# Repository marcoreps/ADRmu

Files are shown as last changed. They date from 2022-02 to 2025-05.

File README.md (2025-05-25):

# ADR1000 10V standard

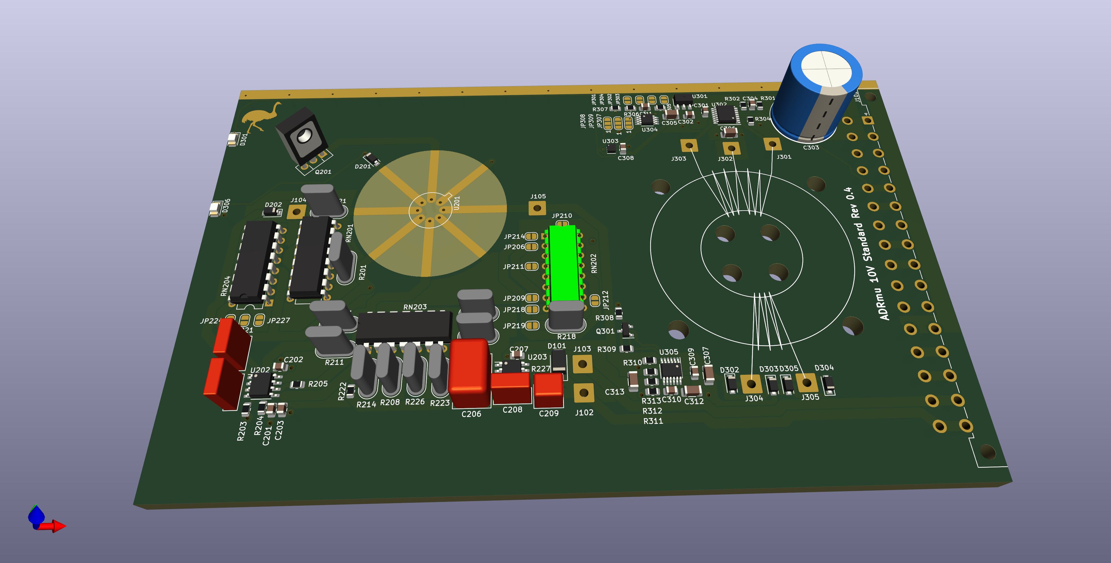
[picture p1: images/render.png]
rendering

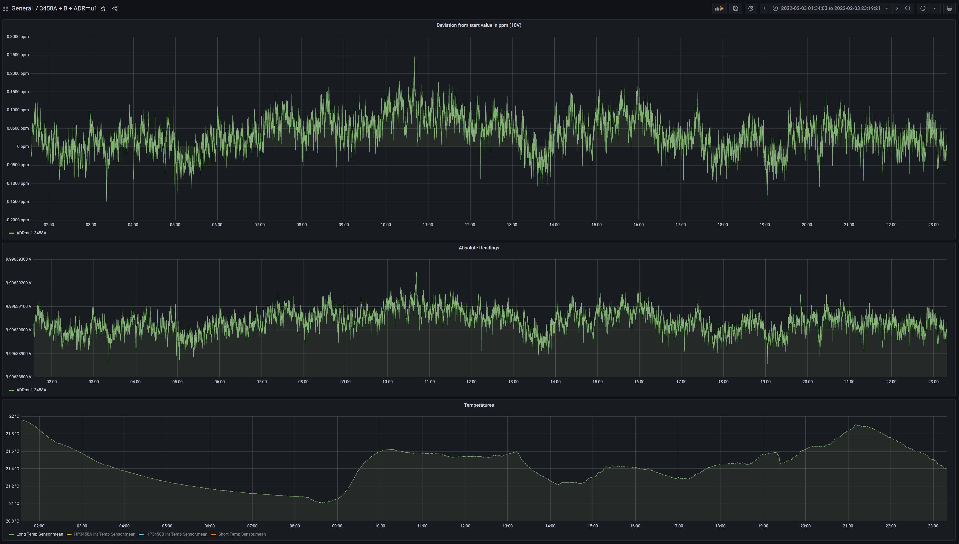
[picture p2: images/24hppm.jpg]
ppm over 24h

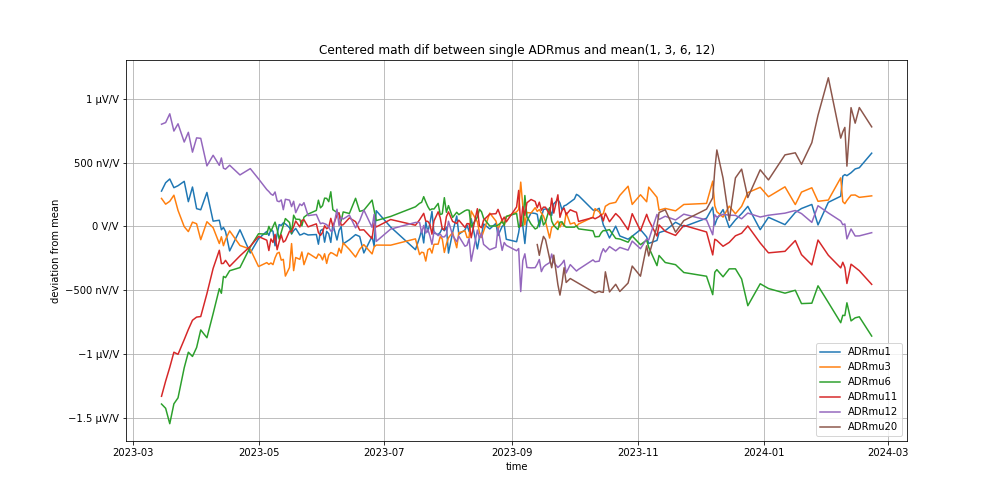
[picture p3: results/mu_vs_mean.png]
one year drift


## Scope

Low cost 10V DC reference standard in DIN 41612 modular enclosure. Based on ovenized LTZ1000 / LTZ1000A or ADR1000A zener diodes. Fits into standard 100x160mm project boxes too. The most promising strategies for configuring the zener and buffering the output are accommodated. Includes a high isolation DC-DC converter to attenuate the effects of common mode current.

## TODO

Align JP and R designators

Remove JPB and JPH enumeration

add lt5400 and other gain resistor options

discrete push-pull driver

snubber for the DC-DC converter?

## Assembly advice

Recommended 5:7 transformer (pri:sec) when using 12V input

## Spec speculations

After initial settling, tempco adjustment, continuously powered on, no ambient temperatures outside of specified range

### Output Voltage Stability (± µV/V):

24 hour: < 0.3

30 day: < 0.4

90 day: < 0.8

1 year: < 1.0

### Output Voltage Noise (0.1 - 10 Hz)(±µV/V rms)

< 0.02

### Output Voltage Tempco (±µV/V/K)

< 0.04

### Short circuit current (mA)

9-11

### Power consumption (W)

\< 2W

### Isolation (to DCin, Chassis)

\> 10 000 MΩ

< 1000 pF

### Output Protection

Output can be shorted indefinitely with battery life derating. Output protected against ESD and input up to 60V.

### Specified Temperature Range (°C)

15 - 35

### Oerational Temperature Range (°C)

-10 - 40

## Measured results
| SN    | U202  | .1-10Hz Noise   | Tempco 15-35°C    |  24h Stab  |  30d Stab  |  90d Stab  |  1yr Stab  |
| ---   | ----  | --------------  | ---------------   | ---------- | ---------- | ---------- | ---------- |
|       |       | \[µV/V rms\]    | \[µV/V/k\]        | \[µV/V\]   | \[µV/V\]   | \[µV/V\]   | \[µV/V\]   |
|   1   | ADR   | [0.0139][1]     |                   | 0.25       | 0.4        |            |            |
| ~~2~~ |~~LTZ-A~~| ~~[0.0175][2]~~|                  |            |            |            |            |
|   3   | LTZ-A | [0.0201][3]     | [-0.024][3tc]     |            |            |            |            |
|   4   |ADR1001| [0.0275][4]     | [-0.133][4tc]     |            |            |            |            |
| ~~5~~ |~~ADR~~|~~[0.0119][5]~~  |~~[+0.015][5tc]~~  |            |            |            |            |
| ~~7~~ |~~ADR~~|~~[0.0125][7]~~  |~~[+0.032][7tc]~~  |            |            |            |            |
|   9   |  ADR  |  [0.0121][9]    |  [+0.156][9tc]    |            |            |            |            |
|~~107~~|~~ADR~~|                 |~~[+0.049][107tc]~~|            |            |            |            |
|~~108~~|~~ADR~~|~~[0.0163][108]~~|~~[+0.030][108tc]~~|            |            |            |            |
|~~10~~ |~~ADR~~|~~[0.0115][10]~~ |~~[-0.028][10tc]~~ |            |            |            |            |
|  11   | ADR   | [0.0129][11]    | [+0.015][11tc]    |            |            |            |            |
|  12   | ADR   | [0.0116][12]    |                   |            |            |            |            |
|~~13~~ |~~ADR~~|~~[0.0132][13]~~ |~~[-0.024][13tc]~~ |            |            |            |            |
|~~F731B~~  |~~DH80417B~~| ~~[0.0272][731]~~  |       |            |            |            |            |
|   6   | ADR   |                 | [-0.018][6tc]     |            |            |            |            |
|~~14~~ |~~LTZ-A~~|               |~~[+0.025][14tc]~~ |            |            |            |            |
|  15   |  ADR  |   [0.0123][15]  |                   |            |            |            |            |
|  20   | LTZ-A |                 | -0.018            |            |            |            |            |
 
[1]:/results/ADRmu1_LFnoise.png
[2]:/results/ADRmu2_LFnoise.png
[3]:/results/ADRmu3_LFnoise.png
[4]:/results/ADRmu4_LFnoise_improved.png
[5]:/results/ADRmu5_LFnoise.png
[7]:/results/ADRmu7_LFnoise.png
[9]:/results/ADRmu9_LFnoise.png
[10]:/results/ADRmu10_LFnoise.png
[11]:/results/ADRmu11_LFnoise.png
[12]:/results/ADRmu12_LFnoise.png
[13]:/results/ADRmu13_LFnoise.png
[13]:/results/ADRmu15_LFnoise.png
[108]:/results/ADRmu108_LFnoise.png
[731]:/results/Fluke731B_LFnoise.png

[3tc]:/results/ADRmu3_TC.ipynb
[4tc]:/results/ADRmu4_TC.ipynb
[5tc]:/results/ADRmu5_TC.ipynb
[7tc]:/results/ADRmu7_TC.ipynb
[9tc]:/results/ADRmu9_TC.ipynb
[10tc]:/results/ADRmu10_TC.ipynb
[11tc]:/results/ADRmu11_TC.ipynb
[12tc]:/results/ADRmu12_TC.ipynb
[13tc]:/results/ADRmu13_TC.ipynb
[107tc]:/results/ADRmu107_TC.ipynb
[108tc]:/results/ADRmu108_TC.ipynb
[14tc]:/results/ADRmu14_TC.ipynb
[6tc]:/results/ADRmu6_TC.ipynb

Strikethrough: Device no longer in my possession

## Initial drift & burn-in
| SN  | PCB  |      U202      | Powered on | Preparation | Initial ΔV | Hours to plateau | .1-10Hz noise before | Special |
| --- | ---- | -------------- | ---------- | ----------- | ---------- | ---------------- | -------------------- |---------|
|   1 | 0.4  | ADR1000A 2017  | Jul 2021   |1yr dummy circuit| no data|                  |                      | VPG golden network |
|   2 | 0.4  |    LTZ1000A    | Apr 2022   | none        | no data    |                  |                      | LTZ1000A w/ VPG foil |
|   3 | 0.5  |    LTZ1000A    | Mar 2022   | none        | no data    |                  |                      | Cheapest LTZ variant |
|   4 |0.5SE |    ADR10001    | May 2022   | none        | no data    |                  |                      | ~~Popcorn noise~~ Healed? |
|   5 | 0.9  | ADR1000A 2022  | Jan 2023   | 7d 150°C b&b|            |                  |                      | Gone to new owner |
|   7 | 0.9  | ADR1000A 2022  | Jan 2023   | 7d 150°C b&b|            |                  |                      | No trim resistors |
|   9 | 0.9  | ADR1000A 2022  | Jan 2023   | none        | 1.1 µV/V   | 310              |                      | VPG golden network |
| 107 | 0.9  | ADR1000A 2018  | Dec 2022   | none        | 3.8 µV/V   | 640              |                      | Transplant to 108 |
| 108 | 0.9  | ADR1000A 2018  | Dec 2022   | none        | 3.8 µV/V   | 640              |                      | Gone to new owner |
|  10 | 0.9  | ADR1000A 2022  | Feb 2023   | none        |            |                  |                      | On/off cylcing 48h |
|  11 | 0.9  | ADR1000A 2022  | Feb 2023   |7d dummy circuit|         |                  |                      | No trim resistors |
|  12 | 0.9  | ADR1000A 2022  | Feb 2023   |7d in situ b&b|           |                  |                      | On/off cylcing 24h |
|  13 | 0.9  | ADR1000A 2022  | Feb 2023   |             |            |                  |                      | Ultrasonic cleaned |
|   6 | 1.1  | ADR1000A 2022  | Mar 2023   |30d dummy circuit|        |                  |                      | Chinese SMT assembly |
|  14 | 1.1  | LTZ1000A 2020  | Mar 2023   | none        |            |                  |                      | Chinese SMT assembly |
|  15 | 1.1  | LTZ1000A 2020  | Mar 2023   | none        |            |                  |                      | Chinese SMT assembly |
|  44 | 1.1  | LTZ1000A 2020  | Mar 2023   | none        |            |                  |                      | Chinese SMT assembly |
|  20 | 1.1  | LTZ1000A 2020  | Sep 2023   | none        |            |                  |                      | Chinese SMT assembly |

## Trim levels

The PCB is prepared for various configurations to adapt to different needs and part availabilities. Here's what I have built so far:

| SN  | U202 | R213 / Pin4 | R214 / Pin5 | R220 / Pin3 | Oven divider      | R225 / Iz Down | R223 / Iz Up | 10V gain divider |
| --- | ---- | ----------- | ----------- | ----------- | ----------------- | -------------- | ------------ | ---------------- |
|   1 | ADR  | 1445 95.3R  | 1445 61.9k  | 0R          | 1445 13 ratio     | open           | open         | 1445 2 ratio     |
|   2 |LTZ-A | Z201 100R   | 61.9k  Foil | SMD Foil    | VHD200 13 ratio   |                |              | VHD200 2.5 ratio |
|   3 |LTZ-A | 100R TOMC   | 50k S102    | 100R TOMC/5 | TDP10k 13.5 ratio | open           | 230k RN73    | TDP10k 2.5 ratio |
|   4 |ADR1k1| 100R VHP100T| integrated  | integrated  | integrated        |                |              | integrated       |
|   5 | ADR  | Alpha MCY   | Alpha MAY   | 0R          | TDP10k 11.5 ratio | open           | 470k RN73    | TDP10k 2 ratio   |
|   7 | ADR  | Z201        | Z201        | 0R          | TDP10k            | open           | open         | TDP10k 2 ratio   |
|   9 | ADR  | 1445 95.3R  | 1445 61.9k  | 0R          | 1445 13 ratio     | open           | open         | 1445 2 ratio     |
| 107 | ADR  | Z201T       | Z202T       | 0R          | TOMC10k 11.5 ratio| 200k RN73      | open         | TDP10k 2 ratio   |
| 108 | ADR  | Z201T       | Z202T       | 0R          | TOMC10k 11.5 ratio|                |              | TDP10k 2 ratio   |
|  10 | ADR  | RCK02       | RCK02       | 0R          | TDP10k 11.5 ratio | 493k RN73      | open         | TDP10k 2 ratio   |
|  11 | ADR  | Z201T       | Z201T       | 0R          | TDP10k 11.5 ratio |                |              | TDP10k 2 ratio   |
|  12 | ADR  | RCK02       | RCK02       | 0R          | TDP10k 12 ratio   | 1M             | open         | TDP10k 2 ratio   |
|  13 | ADR  | RCK02       | RCK02       | 0R          | TDP10k 11.5 ratio | open           | 1M           | TDP10k 2 ratio   |
|   6 | ADR  | PTF56       | PTF56       | 0R          | TDP10k 11.5 ratio |                |              | TDP10k 2 ratio   |
|  14 |LTZ-A | TDP         | 1% ax metal | TDP         | TDP10k 12   ratio | open           | open         | TDP10k 2.5 ratio |
|  15 |      |             |             |             |                   |                |              |                  |
|  44 | ADR  | Z201T       | Z202T       | 0R          | TDP10k 11.5 ratio | 900k           | open         | TDP10k 2 ratio   |
|  20 |LTZ-A | 100R TDP    | 40k Prec WW | 16.667R TDP | TDP10k 11.5 ratio | open           | 1M           | TDP10k 2.5 ratio |

## Raw Vz of 10 parts in datasheet default circuit, warmed up for a few minutes but not burnt in
| SN  |   Type  | Datecode |     Vz    | 
| --- | ------- | -------- | --------- |
| \#1 | ADR1000 | 2108     | 6.6556730 |
| \#8 | ADR1000 | 2108     | 6.6545676 |
| \#9 | ADR1000 | 2108     | 6.6531460 |
| \#10| ADR1000 | 2108     | 6.6609841 |
| \#11| ADR1000 | 2108     | 6.6690263 |
| \#12| ADR1000 | 2108     | 6.6534043 |
|   5 | ADR1000 | 2209     | 6.6457519 |
|   8 | ADR1000 | 2209     | 6.6509818 |
|   3 | ADR1000 | 1839     | 6.6707478 |
| \#7 | ADR1000 | 2108     | 6.6545726 |

### ADR1000 & Vishay 1445 All-in-one Resistor Network

My SN 1 is built this way. This is a no-brainer or easy mode. When I got my first glimpse at the ADR1000 datasheet I went straight to Vishay Foil Resistors and ordered an all-in-one resistor network with all the critical resistors from the datasheet plus a simple divider for buffering the 6.62V output to 10V ([Custom network specification][1445]). By specifying at least 2 ppm/°C TC tracking for the two critical dividers I am guaranteed great performance. And thanks to the hermetically sealed DIP14 package I expect little long term drift from the resistors. This solution comes at a hefty price and is not effortlessly adjustable after assembly.

[1445]:/datasheets/322146_p1-4_1445_Marco_Reps.pdf

### LTZ1000A & Discrete Vishay Foil Resistors

My SN 2 is built this way. This is probably the most popular way of building LTZ1000 voltage standards (i.e. [xDevs KX][kx]). Digikey carries quite a few hermetically sealed Vishay Bulk Metal Foil resistors ~~without MOQ these days~~ not any more LAME!, giving you all the design freedom. The two most critical parts are the LTZ-temperature-configuration divider i.e. 13k/1k and the 7.1V to 10V buffer divider i.e. 2k/5k. For these two I used hermetically sealed Vishay VHD200 dividers. These have guaranteed TC tracking and little long term drift. The remaining LTZ-configuration resistors i.e. 70k, 70k, 120R are not very critical. For best performance you can add an additional resistor to LTZ pin 3 to improve the Vrefs tempco, see "Adjusting Temperature Coefficient in Unstabilized Applications" in the LTZ1000 datasheet. 20 Ohm seems to be a reasonable approximation, suitable for most LTZs. In my case I determined 18 Ohm to be an optimal resistor with a TC peak at the oven setpoint. Careful, this additional resistor, if equipped, has a lot of influence on zener voltage and should be of high quality.

[kx]:https://xdevs.com/article/kx-ref/

### LTZ1000A & Thin film arrays

My SN 3 and 20 are built this way. This variant is inspired by Datron Wavetek 7000 DCV Standards ([EEVBlog forum thread][w7000]) and as such it has proven itself over a long time. Here the most critical voltage dividers for the LTZ1000 temperature and the 7->10V gain are implemented through an arrangement of monolithic thin film resistor arrays and their fantastic tracking temperature coefficients. Furthermore the overall output voltage tempco is fine-tuned after assembly through trim resistors R225 / R223. SN 3 is one of the cheapest ADRmus in my comparison, yet one of the most stable ones.

[w7000]:https://www.eevblog.com/forum/metrology/(3300)-wavetek-7000-the-hidden-gemstone/

### ADR1000 & Thin film arrays

Most of my ADRmus are built this way. This is the most cost-effective way to build a great performance 10V DC Standard. The same techniques that worked for LTZ in the past also apply to ADR1000, only the specific resistor values are slightly different. Based on my early ADR1000 samples I can see significantly longer initial settling times of ADR1000, which can be improved simply by power cycling a part in its default circuit (30 minutes off, 30 minutes on for a week). This new part exhibits lower low frequency noise than LTZ. A 10V buffer circuit with a low noise op amp and thin film arrays ([Excess Noise in Thin Film and Metal Foil Resistor Networks][beev]) passes this advantage right on to the output. 

[beev]:https://arxiv.org/abs/2109.02448

### ADR1001

I have been given one very early sample of this new part, so my results may not reflect the final parts performance. This new all-in-one ovenized zener reference & buffer makes it easier than ever before to deploy a high performance, environmentally tolerant voltage reference with few external parts and little research. My sample showed some popcorn noise at first ([Screenshot][popcorn]), which I seemingly improved by keeping the part powered on, externally heated to 110°C for a few weeks. This extreme measure made it impossible to judge early drift. Long-term drift and tempco now seem to fall easily within the datasheet spec. LF noise of the 10V output still appears to be slightly elevated, but the datasheet only specifies this for the 6P6 output. Overall this part is not the greatest performer in my comparison, it lacks a way of fine-tuning, but it's by far the easiest to use and its efficient overall heater makes it interesting for portable devices.

[popcorn]:/results/ADRmu4_LFnoise_popcorn.png

## Results

### Raw data

Unprocessed CSV files can be found here https://github.com/marcoreps/multiinstrumentalist/tree/master/csv These show direct readings by digital voltmeters, which are subject to temperature variations, adjustments and even modifications, resulting in large deviations of readings.

### Processed data

To attenuate voltmeter errors from the measurements, we use the mathematical difference between an ADRmu reading and the average of many ADRmu readings that were taken at the same time, with the same voltmeter. These results can be found here https://github.com/marcoreps/ADRmu/tree/main/results

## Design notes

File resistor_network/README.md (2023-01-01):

## Scope

This is an adapter for up to 8 SMD resistors to fit into a DIP16 footprint. Using this board one could assemble an all-in-one LTZ/ADR configuration and buffering resistor network out of good quality SMD thin film resistors such as RN73. When using a thermally conductive PCB substrate such as Al, Cu, AlN or Al2O3 the resistors are thermally coupled which can be an advantage. When populating the crystal heater circuit and providing it with power, Vref and GND, it will thermally stabilize the resistor networks temperature at around 40°C.

## Result

I have performed only one superficial test with such a network so far and it didn't look as good as the monolithic 8xthin film array method.

## Image

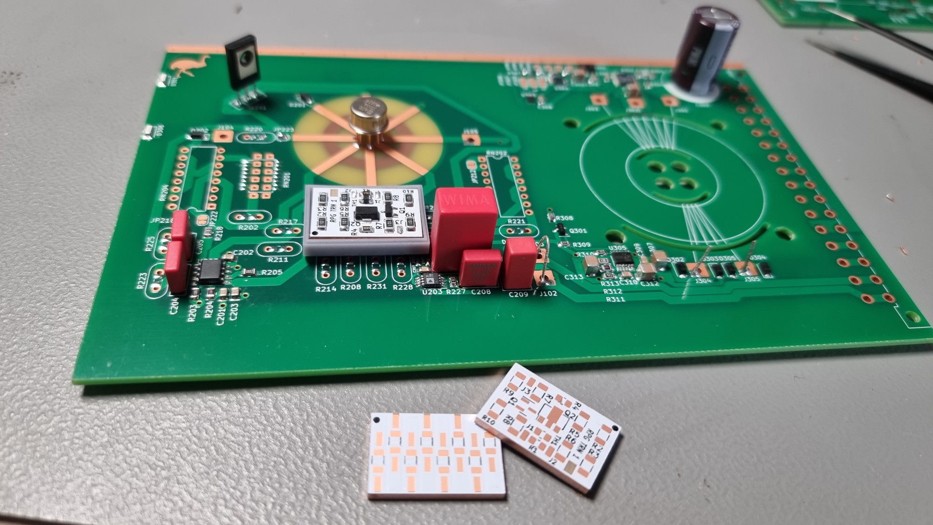
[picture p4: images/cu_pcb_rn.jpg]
serviervorschlag


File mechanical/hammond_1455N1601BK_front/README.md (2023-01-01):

# Careful:

The + / - Cutouts are for special Taobao connectors, too small for Pomona 3770! Adjust to your needs before ordering!

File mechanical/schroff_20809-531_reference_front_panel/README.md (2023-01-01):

# Front panel for Schroff 20809-531 Eurocard cassettes 

Very ugly silk screen, would not recommend this design, but the hole locations fit.

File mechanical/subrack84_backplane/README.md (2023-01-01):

# 4 + 4 Module Backplane

Tested successfully with PROMA 133061 aka https://www.reichelt.com/de/en/system-housing-geh-sg-1-10-p50437.html but should be compatible with many other eurocard subrack enclosures.

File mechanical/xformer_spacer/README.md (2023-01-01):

# DC-DC Transformer spacer for the reference module

Optional part to help reduce inter-winding capacitance, inspired by Mac

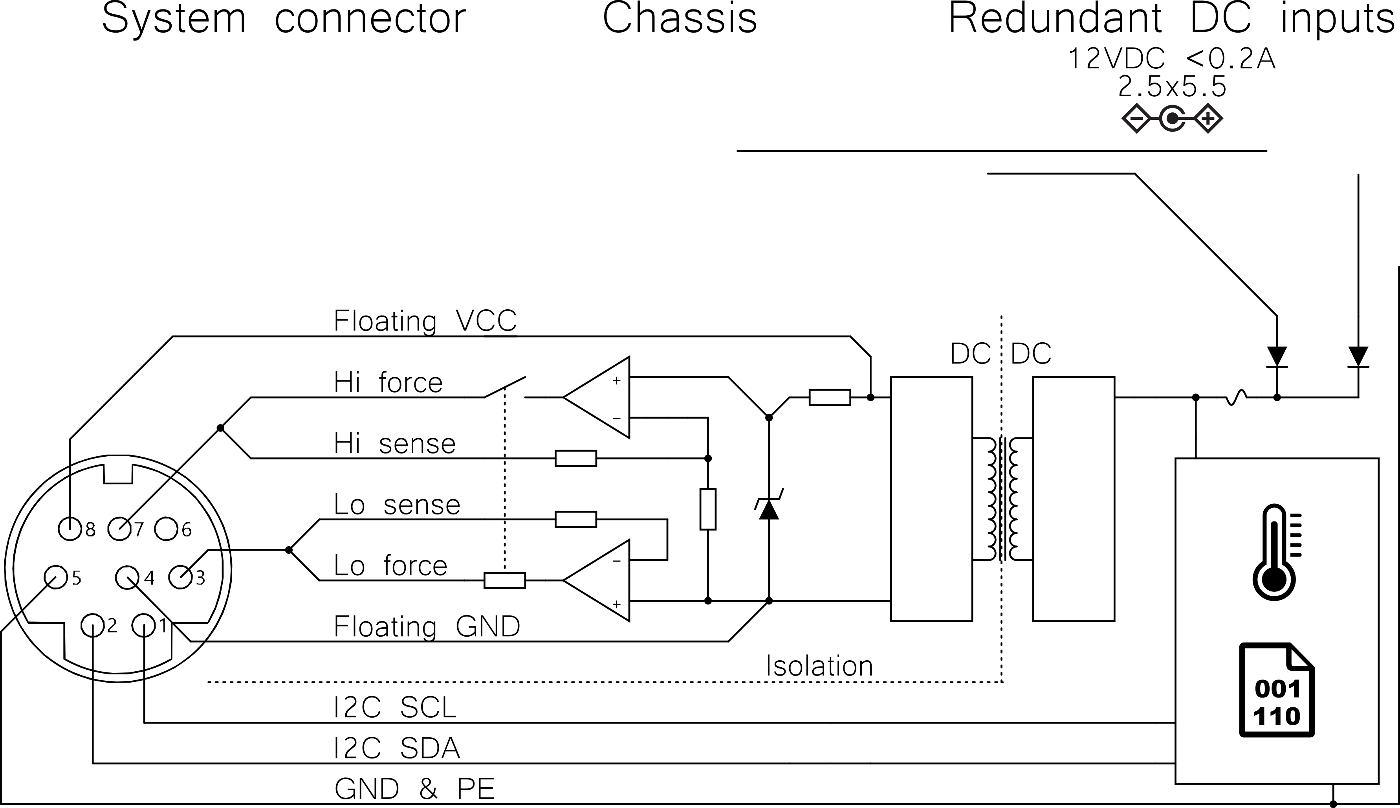
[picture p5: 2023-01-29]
mechanical/hammond_1455N1601BK_back/drawing.png

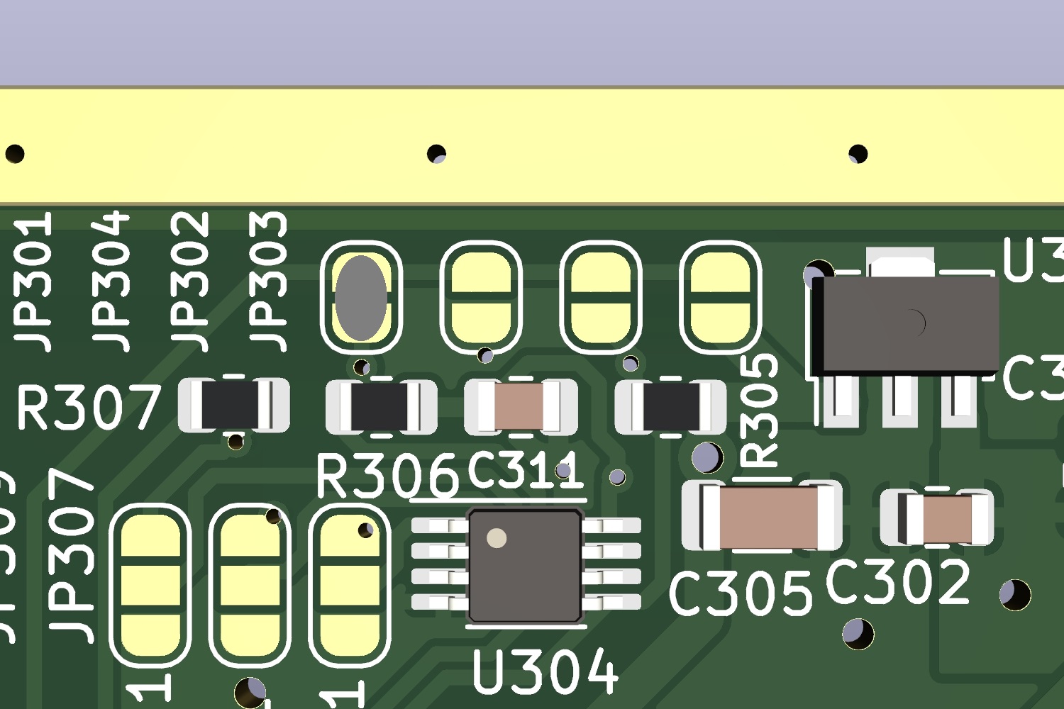
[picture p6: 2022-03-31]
images/TMP117_address_0x4B.jpg

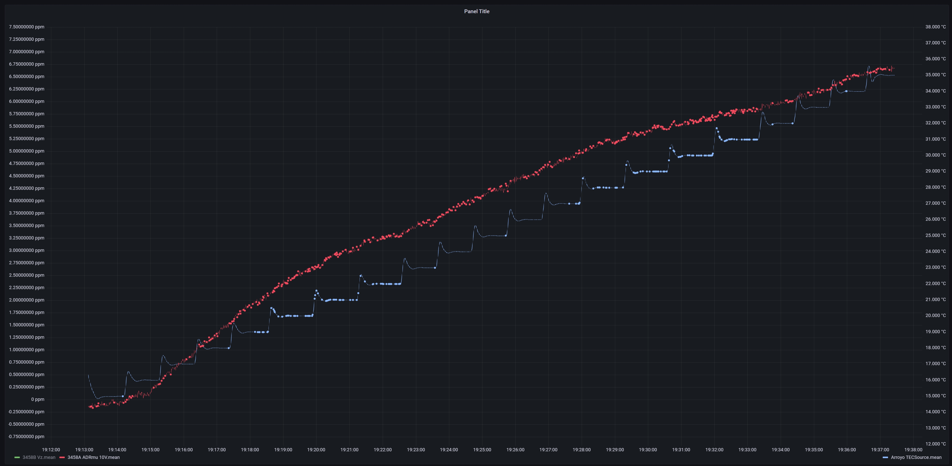
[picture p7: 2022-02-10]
images/tc_10V.jpg

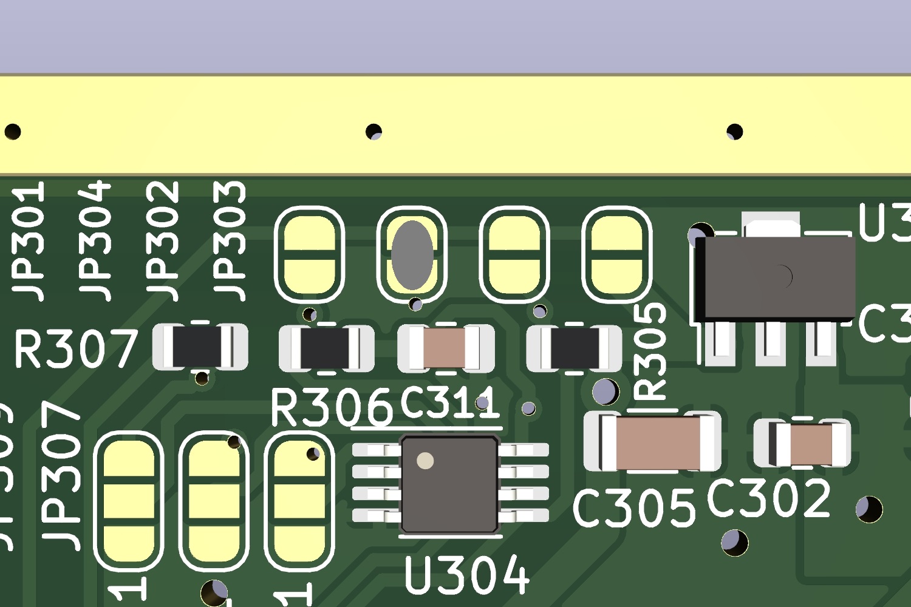
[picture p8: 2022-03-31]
images/TMP117_address_0x48.jpg

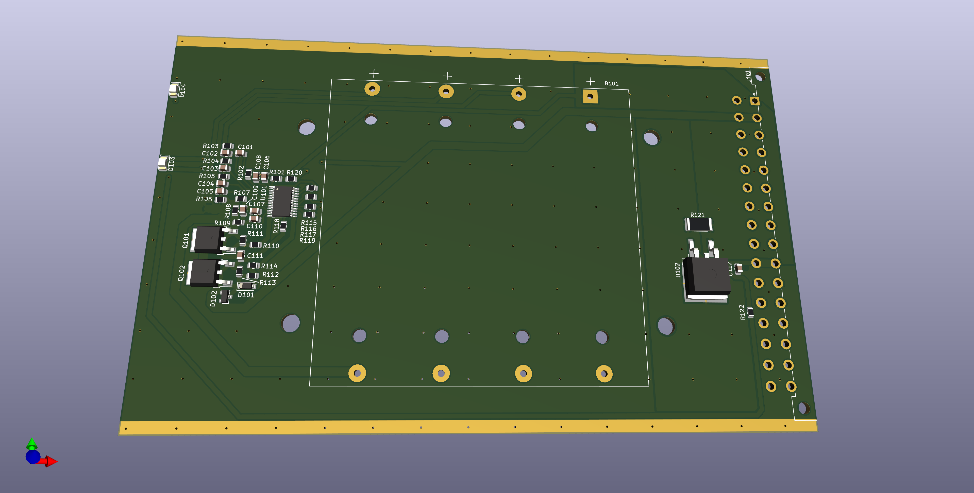
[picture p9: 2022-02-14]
images/ADRmu_battery_render.png

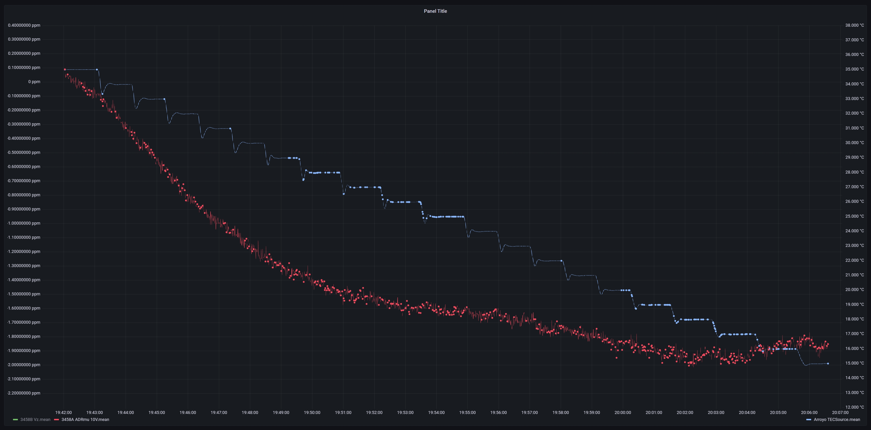
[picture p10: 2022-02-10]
images/tc_raw_ADR.jpg

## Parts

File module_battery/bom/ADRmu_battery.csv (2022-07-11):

Source: | C:\Users\reps\Documents\ADRmu\module_battery\ADRmu_battery.kicad_sch
Date: | 11/07/2022 09:41:18
Tool: | Eeschema (6.0.5)
Generator: | C:\Program Files\KiCad\6.0\bin\scripting\plugins/bom_csv_grouped_by_value.py
Component Count: | 78
Individual Components:
Item | Qty | Reference(s) | Value | LibPart | Footprint | Datasheet
 |  | B101 | BK-18650-PC8 | ADRmu_battery_Library:BK-18650-PC8 | ADRmu_battery_Library:BK-18650-PC8
 |  | C101 | 1u 50V | Device:C | Capacitor_SMD:C_0805_2012Metric | ~
 |  | C102 | 1u 50V | Device:C | Capacitor_SMD:C_0805_2012Metric | ~
 |  | C103 | 1u 50V | Device:C | Capacitor_SMD:C_0805_2012Metric | ~
 |  | C104 | 1u 50V | Device:C | Capacitor_SMD:C_0805_2012Metric | ~
 |  | C105 | 1u 50V | Device:C | Capacitor_SMD:C_0805_2012Metric | ~
 |  | C106 | 1u 50V | Device:C | Capacitor_SMD:C_0805_2012Metric | ~
 |  | C107 | 100n 50V | Device:C | Capacitor_SMD:C_0805_2012Metric | ~
 |  | C108 | 1u 50V | Device:C | Capacitor_SMD:C_0805_2012Metric | ~
 |  | C109 | 100n 50V | Device:C | Capacitor_SMD:C_0805_2012Metric | ~
 |  | C110 | 100n 50V | Device:C | Capacitor_SMD:C_0805_2012Metric | ~
 |  | C111 | 100n 50V | Device:C | Capacitor_SMD:C_0805_2012Metric | ~
 |  | C112 | 100n 50V | Device:C | Capacitor_SMD:C_0805_2012Metric | ~
 |  | C113 | 220u 16V | Device:C_Polarized | Capacitor_THT:CP_Radial_D10.0mm_P5.00mm | ~
 |  | C114 | 1u 50V | Device:C | Capacitor_SMD:C_0805_2012Metric | ~
 |  | C115 | 1u 50V | Device:C | Capacitor_SMD:C_0805_2012Metric | ~
 |  | C116 | 1u 50V | Device:C | Capacitor_SMD:C_0805_2012Metric | ~
 |  | C117 | 100n 50V | Device:C | Capacitor_SMD:C_0805_2012Metric | ~
 |  | D101 | 1N4148 | Device:D | Diode_SMD:D_SOD-123 | ~
 |  | D102 | 16V | Device:D_Zener | Diode_SMD:D_SOT-23_ANK | ~
 |  | D103 | LT Y8SG-V2AB-36 | Device:LED | LED_SMD:LED_1206_3216Metric | ~
 |  | D104 | LT Y8SG-V2AB-36 | Device:LED | LED_SMD:LED_1206_3216Metric | ~
 |  | D105 | BZX84C10 | Diode:BZX84Cxx | Package_TO_SOT_SMD:SOT-23 | https://diotec.com/tl_files/diotec/files/pdf/datasheets/bzx84c2v4.pdf
 |  | D106 | LT Y8SG-V2AB-36 | Device:LED | LED_SMD:LED_1206_3216Metric | ~
 |  | D109 | LT Y8SG-V2AB-36 | Device:LED | LED_SMD:LED_1206_3216Metric | ~
 |  | D112 | LT Y8SG-V2AB-36 | Device:LED | LED_SMD:LED_1206_3216Metric | ~
 |  | D116 | RS1D-13-F | Device:D_Schottky | Diode_SMD:D_SMA | ~
 |  | F101 | 2A | Device:Polyfuse | Fuse:Fuse_1812_4532Metric | ~
 |  | HS101 | THJP1206AST1 | Device:C | Capacitor_SMD:C_1206_3216Metric | ~
 |  | HS102 | THJP1206AST1 | Device:C | Capacitor_SMD:C_1206_3216Metric | ~
 |  | HS103 | THJP1206AST1 | Device:C | Capacitor_SMD:C_1206_3216Metric | ~
 |  | HS104 | THJP1206AST1 | Device:C | Capacitor_SMD:C_1206_3216Metric | ~
 |  | J101 | Harting 09042326831 | Connector:DIN41612_02x16_AC_EvenPins | Connector_DIN:DIN41612_D_2x16_Male_Horizontal_THT | ~
 |  | Q101 | Q_NMOS_GDS | Device:Q_NMOS_GDS | Package_TO_SOT_SMD:TO-252-2 | ~
 |  | Q102 | Q_NMOS_GDS | Device:Q_NMOS_GDS | Package_TO_SOT_SMD:TO-252-2 | ~
 |  | R101 | 1k | Device:R | Resistor_SMD:R_0805_2012Metric | ~
 |  | R102 | 33 | Device:R | Resistor_SMD:R_0805_2012Metric | ~
 |  | R103 | 33 | Device:R | Resistor_SMD:R_0805_2012Metric | ~
 |  | R104 | 33 | Device:R | Resistor_SMD:R_0805_2012Metric | ~
 |  | R105 | 33 | Device:R | Resistor_SMD:R_0805_2012Metric | ~
 |  | R106 | 33 | Device:R | Resistor_SMD:R_0805_2012Metric | ~
 |  | R107 | 100 | Device:R | Resistor_SMD:R_0805_2012Metric | ~
 |  | R108 | 60mR | Device:R | Resistor_SMD:R_0805_2012Metric | ~
 |  | R109 | 100 | Device:R | Resistor_SMD:R_0805_2012Metric | ~
 |  | R110 | 5k1 | Device:R | Resistor_SMD:R_0805_2012Metric | ~
 |  | R111 | 10M | Device:R | Resistor_SMD:R_0805_2012Metric | ~
 |  | R112 | 1M | Device:R | Resistor_SMD:R_0805_2012Metric | ~
 |  | R113 | 3M | Device:R | Resistor_SMD:R_0805_2012Metric | ~
 |  | R114 | 5k1 | Device:R | Resistor_SMD:R_0805_2012Metric | ~
 |  | R115 | 10k | Device:R | Resistor_SMD:R_0805_2012Metric | ~
 |  | R116 | 10k | Device:R | Resistor_SMD:R_0805_2012Metric | ~
 |  | R117 | 200k | Device:R | Resistor_SMD:R_0805_2012Metric | ~
 |  | R118 | 470k | Device:R | Resistor_SMD:R_0805_2012Metric | ~
 |  | R119 | 10k | Device:R | Resistor_SMD:R_0805_2012Metric | ~
 |  | R120 | 49k9 | Device:R | Resistor_SMD:R_0805_2012Metric | ~
 |  | R121 | 9.1M | Device:R | Resistor_SMD:R_0805_2012Metric | ~
 |  | R122 | 680k | Device:R | Resistor_SMD:R_0805_2012Metric | ~
 |  | R124 | 1k2 | Device:R | Resistor_SMD:R_0805_2012Metric | ~
 |  | R125 | 49k9 | Device:R | Resistor_SMD:R_0805_2012Metric | ~
 |  | R126 | 49k9 | Device:R | Resistor_SMD:R_0805_2012Metric | ~
 |  | R127 | 49k9 | Device:R | Resistor_SMD:R_0805_2012Metric | ~
 |  | R128 | 49k9 | Device:R | Resistor_SMD:R_0805_2012Metric | ~
 |  | R129 | 10k | Device:R | Resistor_SMD:R_0805_2012Metric | ~
 |  | R130 | 5k1 | Device:R | Resistor_SMD:R_0805_2012Metric | ~
 |  | R131 | 10k | Device:R | Resistor_SMD:R_0805_2012Metric | ~
 |  | R132 | 22k | Device:R | Resistor_SMD:R_0805_2012Metric | ~
 |  | R133 | 6k8 | Device:R | Resistor_SMD:R_0805_2012Metric | ~
 |  | R134 | 6k8 | Device:R | Resistor_SMD:R_0805_2012Metric | ~
 |  | R135 | 82k | Device:R | Resistor_SMD:R_0805_2012Metric | ~
 |  | R136 | 10k | Device:R | Resistor_SMD:R_0805_2012Metric | ~
 |  | R137 | 10k | Device:R | Resistor_SMD:R_0805_2012Metric | ~
 |  | TH101 | CMFB3435103FNT | Device:Thermistor_NTC | Resistor_SMD:R_0805_2012Metric | ~
 |  | TH102 | Alternative 10k NTC | Device:Thermistor_NTC | Resistor_THT:R_Axial_DIN0204_L3.6mm_D1.6mm_P2.54mm_Vertical | ~
 |  | U101 | BQ7791500 | ADRmu_battery_Library:BQ77915 | Package_SO:TSSOP-24_4.4x7.8mm_P0.65mm | https://www.ti.com/lit/ds/symlink/bq77915.pdf
 |  | U102 | LTC4079 | ADRmu_battery_Library:LTC4079 | Package_DFN_QFN:DFN-10-1EP_3x3mm_P0.5mm_EP1.65x2.38mm | https://www.analog.com/media/en/technical-documentation/data-sheets/ltc4079.pdf
 |  | U103 | L7812 | Regulator_Linear:L7812 | Package_TO_SOT_SMD:TO-252-2 | http://www.st.com/content/ccc/resource/technical/document/datasheet/41/4f/b3/b0/12/d4/47/88/CD00000444.pdf/files/CD00000444.pdf/jcr:content/translations/en.CD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
 |  | U104 | LM317_TO-263 | Regulator_Linear:LM317_TO-263 | Package_TO_SOT_SMD:TO-263-2 | http://www.ti.com/lit/ds/symlink/lm317.pdf
 |  | U105 | LM339 | Comparator:LM339 | Package_SO:SOIC-14_3.9x8.7mm_P1.27mm | https://www.st.com/resource/en/datasheet/lm139.pdf
Collated Components:
Item | Qty | Reference(s) | Value | LibPart | Footprint | Datasheet
1 | 1 | B101 | BK-18650-PC8 | ADRmu_battery_Library:BK-18650-PC8 | ADRmu_battery_Library:BK-18650-PC8
2 | 10 | C101, C102, C103, C104, C105, C106, C108, C114, C115, C116 | 1u 50V | Device:C | Capacitor_SMD:C_0805_2012Metric | ~
3 | 6 | C107, C109, C110, C111, C112, C117 | 100n 50V | Device:C | Capacitor_SMD:C_0805_2012Metric | ~
4 | 1 | C113 | 220u 16V | Device:C_Polarized | Capacitor_THT:CP_Radial_D10.0mm_P5.00mm | ~
5 | 1 | D101 | 1N4148 | Device:D | Diode_SMD:D_SOD-123 | ~
6 | 1 | D102 | 16V | Device:D_Zener | Diode_SMD:D_SOT-23_ANK | ~
7 | 5 | D103, D104, D106, D109, D112 | LT Y8SG-V2AB-36 | Device:LED | LED_SMD:LED_1206_3216Metric | ~
8 | 1 | D105 | BZX84C10 | Diode:BZX84Cxx | Package_TO_SOT_SMD:SOT-23 | https://diotec.com/tl_files/diotec/files/pdf/datasheets/bzx84c2v4.pdf
9 | 1 | D116 | RS1D-13-F | Device:D_Schottky | Diode_SMD:D_SMA | ~
10 | 1 | F101 | 2A | Device:Polyfuse | Fuse:Fuse_1812_4532Metric | ~
11 | 4 | HS101, HS102, HS103, HS104 | THJP1206AST1 | Device:C | Capacitor_SMD:C_1206_3216Metric | ~
12 | 1 | J101 | Harting 09042326831 | Connector:DIN41612_02x16_AC_EvenPins | Connector_DIN:DIN41612_D_2x16_Male_Horizontal_THT | ~
13 | 2 | Q101, Q102 | Q_NMOS_GDS | Device:Q_NMOS_GDS | Package_TO_SOT_SMD:TO-252-2 | ~
14 | 1 | R101 | 1k | Device:R | Resistor_SMD:R_0805_2012Metric | ~
15 | 5 | R102, R103, R104, R105, R106 | 33 | Device:R | Resistor_SMD:R_0805_2012Metric | ~
16 | 2 | R107, R109 | 100 | Device:R | Resistor_SMD:R_0805_2012Metric | ~
17 | 1 | R108 | 60mR | Device:R | Resistor_SMD:R_0805_2012Metric | ~
18 | 3 | R110, R114, R130 | 5k1 | Device:R | Resistor_SMD:R_0805_2012Metric | ~
19 | 1 | R111 | 10M | Device:R | Resistor_SMD:R_0805_2012Metric | ~
20 | 1 | R112 | 1M | Device:R | Resistor_SMD:R_0805_2012Metric | ~
21 | 1 | R113 | 3M | Device:R | Resistor_SMD:R_0805_2012Metric | ~
22 | 7 | R115, R116, R119, R129, R131, R136, R137 | 10k | Device:R | Resistor_SMD:R_0805_2012Metric | ~
23 | 1 | R117 | 200k | Device:R | Resistor_SMD:R_0805_2012Metric | ~
24 | 1 | R118 | 470k | Device:R | Resistor_SMD:R_0805_2012Metric | ~
25 | 5 | R120, R125, R126, R127, R128 | 49k9 | Device:R | Resistor_SMD:R_0805_2012Metric | ~
26 | 1 | R121 | 9.1M | Device:R | Resistor_SMD:R_0805_2012Metric | ~
27 | 1 | R122 | 680k | Device:R | Resistor_SMD:R_0805_2012Metric | ~
28 | 1 | R124 | 1k2 | Device:R | Resistor_SMD:R_0805_2012Metric | ~
29 | 1 | R132 | 22k | Device:R | Resistor_SMD:R_0805_2012Metric | ~
30 | 2 | R133, R134 | 6k8 | Device:R | Resistor_SMD:R_0805_2012Metric | ~
31 | 1 | R135 | 82k | Device:R | Resistor_SMD:R_0805_2012Metric | ~
32 | 1 | TH101 | CMFB3435103FNT | Device:Thermistor_NTC | Resistor_SMD:R_0805_2012Metric | ~
33 | 1 | TH102 | Alternative 10k NTC | Device:Thermistor_NTC | Resistor_THT:R_Axial_DIN0204_L3.6mm_D1.6mm_P2.54mm_Vertical | ~
34 | 1 | U101 | BQ7791500 | ADRmu_battery_Library:BQ77915 | Package_SO:TSSOP-24_4.4x7.8mm_P0.65mm | https://www.ti.com/lit/ds/symlink/bq77915.pdf
35 | 1 | U102 | LTC4079 | ADRmu_battery_Library:LTC4079 | Package_DFN_QFN:DFN-10-1EP_3x3mm_P0.5mm_EP1.65x2.38mm | https://www.analog.com/media/en/technical-documentation/data-sheets/ltc4079.pdf
36 | 1 | U103 | L7812 | Regulator_Linear:L7812 | Package_TO_SOT_SMD:TO-252-2 | http://www.st.com/content/ccc/resource/technical/document/datasheet/41/4f/b3/b0/12/d4/47/88/CD00000444.pdf/files/CD00000444.pdf/jcr:content/translations/en.CD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
37 | 1 | U104 | LM317_TO-263 | Regulator_Linear:LM317_TO-263 | Package_TO_SOT_SMD:TO-263-2 | http://www.ti.com/lit/ds/symlink/lm317.pdf
38 | 1 | U105 | LM339 | Comparator:LM339 | Package_SO:SOIC-14_3.9x8.7mm_P1.27mm | https://www.st.com/resource/en/datasheet/lm139.pdf

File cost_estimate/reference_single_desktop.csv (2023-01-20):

Item | Qty | Reference(s) | Value | Datasheet | MPN | URL | Price (US$) | Price * Qty
1 | 21 | C201, C202, C203, C204, C205, C301, C302, C308, C309, C310, C311, C314, C315, C317, C318, C402, C403, C405, C406, C410, C411 | 100n 50V | ~ | CL10B104KB8NNWC | https://www.digikey.com/en/products/detail/samsung-electro-mechanics/CL10B104KB8NNWC/3887593 | $0.10 | $2.10
2 | 1 | C303 | 470u 25V | ~ | 25YXF2200MEFCGC16X25 | https://www.digikey.com/en/products/detail/rubycon/25YXF2200MEFCGC16X25/3567077 | $1.26 | $1.26
3 | 1 | C304 | 1n 50V | ~ | C0805C102K5GECAUTO | https://www.digikey.com/en/products/detail/kemet/C0805C102K5GECAUTO/8647414 | $0.21 | $0.21
4 | 6 | C305, C306, C307, C312, C313, C316 | 22u 25V | ~ | CL31A226KAHNNNE | https://www.digikey.com/en/products/detail/samsung-electro-mechanics/CL31A226KAHNNNE/3888705 | $0.36 | $2.16
5 | 1 | C401 | 470n Film | ~ | MKS2C034701C00MSSD | https://www.digikey.com/en/products/detail/wima/MKS2C034701C00MSSD/9370562 | $0.73 | $0.73
6 | 1 | C404 | 10u Film | ~ | MKS2B051001N00JSSD | https://www.digikey.com/en/products/detail/wima/MKS2B051001N00JSSD/9370551 | $3.84 | $3.84
7 | 3 | C408, C409, C413 | 100n Film | ~ | MKS2D031001A00MSSD | https://www.digikey.com/en/products/detail/wima/MKS2D031001A00MSSD/9370574 | $0.48 | $1.44
8 | 2 | C412, C414 | 1u Film | ~ | MKS0B041000F00MSSD | https://www.digikey.com/en/products/detail/wima/MKS0B041000F00MSSD/9370525 | $1.61 | $3.22
9 | 7 | D102, D103, D302, D303, D304, D305, D307 | PMEG6010CEH | ~ | DSS14U | https://www.digikey.com/en/products/detail/smc-diode-solutions/DSS14U/8341859 | $0.22 | $1.54
10 | 2 | D201, D202 | 1N4148 | ~ | 1N4148W | https://www.digikey.com/en/products/detail/smc-diode-solutions/1N4148W/6022450 | $0.14 | $0.28
11 | 2 | D301, D306 | LT Y8SG-V2AB-36 | https://media.digikey.com/pdf/Data%20Sheets/Lite-On%20PDFs/LTST-S321KGKT.pdf | LTST-S321KGKT | https://www.digikey.com/en/products/detail/liteon/LTST-S321KGKT/2764970 | $0.33 | $0.66
12 | 1 | D308 | SMAJ18A-13-F | ~ | SMAJ18A-13-F | https://www.digikey.com/en/products/detail/diodes-incorporated/SMAJ18A-13-F/814796 | $0.39 | $0.39
13 | 1 | F301 | SF-0603S040-2 | https://www.bourns.com/docs/product-datasheets/sf0603s.pdf | SF-0603S040-2 | https://www.digikey.com/en/products/detail/bourns-inc/SF-0603S040-2/8747904 | $0.58 | $0.58
14 | 1 | Q201 | BD135 | http://www.st.com/internet/com/TECHNICAL_RESOURCES/TECHNICAL_LITERATURE/DATASHEET/CD00001225.pdf | BD13510STU | https://www.digikey.com/en/products/detail/onsemi/BD13510STU/975638 | $0.77 | $0.77
15 | 3 | Q301, Q303, Q401 | MMBT3904 | https://www.onsemi.com/pub/Collateral/2N3903-D.PDF | MMBT3904-7-F | https://www.digikey.com/en/products/detail/diodes-incorporated/MMBT3904-7-F/814494 | $0.13 | $0.39
16 | 1 | Q302 | MMBT3906 | https://www.onsemi.com/pub/Collateral/2N3906-D.PDF | MMBT3906-7-F | https://www.digikey.com/en/products/detail/diodes-incorporated/MMBT3906-7-F/770797 | $0.13 | $0.13
17 | 4 | R203, R310, R401, R412 | 1k | ~ | RR1220P-102-D | https://www.digikey.com/en/products/detail/susumu/RR1220P-102-D/432291 | $0.16 | $0.64
18 | 1 | R204 | 1M | ~ | CRG0805F1M0 | https://www.digikey.com/en/products/detail/te-connectivity-passive-product/CRG0805F1M0/2380864 | $0.10 | $0.10
19 | 7 | R205, R234, R301, R314, R315, R316, R317 | 10k | ~ | RR1220P-103-D | https://www.digikey.com/en/products/detail/susumu/RR1220P-103-D/432315 | $0.16 | $1.12
20 | 1 | R218 | 30k | ~ | RR1220P-303-D | https://www.digikey.com/en/products/detail/susumu/RR1220P-303-D/432326 | $0.16 | $0.16
21 | 2 | R221, R318 | DNP | ~ |  |  |  | $0.00
22 | 2 | R302, R304 | 16k9 | ~ | RR1220P-1692-D-M | https://www.digikey.com/en/products/detail/susumu/RR1220P-1692-D-M/676484 | $0.16 | $0.32
23 | 1 | R303 | 49.9k | ~ | RT0805FRE0749K9L | https://www.digikey.com/en/products/detail/yageo/RT0805FRE0749K9L/1079283 | $0.10 | $0.10
24 | 5 | R305, R306, R307, R308, R406 | 4k99 | ~ | RR1220P-4991-D-M | https://www.digikey.com/en/products/detail/susumu/RR1220P-4991-D-M/432569 | $0.16 | $0.80
25 | 1 | R309 | 200k | ~ | RR1220P-204-D | https://www.digikey.com/en/products/detail/susumu/RR1220P-204-D/432346 | $0.16 | $0.16
26 | 1 | R311 | 130k | ~ | RR1220P-134-D | https://www.digikey.com/en/products/detail/susumu/RR1220P-134-D/432342 | $0.16 | $0.16
27 | 1 | R312 | 750k | ~ | RT0805FRE07750KL | https://www.digikey.com/en/products/detail/yageo/RT0805FRE07750KL/1035152 | $0.10 | $0.10
28 | 1 | R313 | 18k | ~ | RR1220P-183-D | https://www.digikey.com/en/products/detail/susumu/RR1220P-183-D/432321 | $0.16 | $0.16
29 | 1 | R409 | 62R | ~ | RT0805FRE0762RL | https://www.digikey.com/en/products/detail/yageo/RT0805FRE0762RL/1079353 | $0.10 | $0.10
30 | 1 | R410 | 47R | ~ | RT0805FRE0747RL | https://www.digikey.com/en/products/detail/yageo/RT0805FRE0747RL/1079276 | $0.10 | $0.10
31 | 2 | R411, R415 | 0R | ~ |  |  | $0.00 | $0.00
32 | 1 | SW301 | SW_Push | https://www.ckswitches.com/media/1471/pts645.pdf | PTS645VH31-2 LFS | https://www.digikey.com/en/products/detail/c-k/PTS645VH31-2-LFS/1146771 | $0.14 | $0.14
33 | 1 | T301 | Feryster RTN-40x25x15(M-083) | ~ | RTN-40X25X15(M-083) | https://sklep.feryster.pl/en/nanoperm-cores/18140-RTN-40X25X15M-083-18140.html | $27.25 | $27.25
34 | 1 | U201 | ADR1000 | https://www.analog.com/media/en/technical-documentation/data-sheets/adr1000.pdf | ADR1000AHZ | https://www.analog.com/en/products/adr1000.html#product-overview | $100.00 | $100.00
35 | 1 | U202 | OPA2172 | https://www.ti.com/general/docs/suppproductinfo.tsp?distId=10 | OPA2172ID | https://www.digikey.com/en/products/detail/texas-instruments/OPA2172ID/5125386 | $2.72 | $2.72
36 | 2 | U301, U306 | L78L33_SOT89 | http://www.st.com/content/ccc/resource/technical/document/datasheet/15/55/e5/aa/23/5b/43/fd/CD00000446.pdf/files/CD00000446.pdf/jcr:content/translations/en.CD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 | L78L33ACUTR | https://www.digikey.com/en/products/detail/stmicroelectronics/L78L33ACUTR/585724 | $0.62 | $1.24
37 | 1 | U302 | LT3439 | https://www.analog.com/media/en/technical-documentation/data-sheets/3439fs.pdf | LT3439EFE#TRPBF | https://www.digikey.com/en/products/detail/analog-devices-inc/LT3439EFE-TRPBF/959304 | $10.75 | $10.75
38 | 1 | U303 | TMP117 | https://www.ti.com/lit/ds/symlink/tmp117.pdf | TMP117MAIDRVT | https://www.digikey.com/en/products/detail/texas-instruments/TMP117MAIDRVT/9749240 | $5.10 | $5.10
39 | 1 | U304 | BR24H64FVM | http://ww1.microchip.com/downloads/en/DeviceDoc/21709c.pdf | BR24H64FVM-5ACTR | https://www.digikey.com/en/products/detail/rohm-semiconductor/BR24H64FVM-5ACTR/13684656 | $0.90 | $0.90
40 | 1 | U305 | LT3045xMSE | https://www.analog.com/media/en/technical-documentation/data-sheets/3045fa.pdf | LT3045EMSE#PBF | https://www.digikey.com/en/products/detail/analog-devices-inc/LT3045EMSE-PBF/6234771 | $8.50 | $8.50
41 | 1 | U307 | L79L05_SOT89 | http://www.farnell.com/datasheets/1827870.pdf | MC79L05F-TP | https://www.digikey.com/en/products/detail/micro-commercial-co/MC79L05F-TP/804677 | $0.41 | $0.41
42 | 3 | U401, U403, U404 | ADA4523 | https://www.analog.com/media/en/technical-documentation/data-sheets/ada4523-1.pdf | ADA4523-1BCPZ | https://www.digikey.com/en/products/detail/analog-devices-inc/ADA4523-1BCPZ/13146514 | $3.06 | $9.18
43 | 1 | U402 | ADG5401F | https://www.analog.com/media/en/technical-documentation/data-sheets/adg5401f.pdf | ADG5401FBCPZ-RL7 | https://www.digikey.com/en/products/detail/analog-devices-inc/ADG5401FBCPZ-RL7/13212404 | $7.29 | $7.29
44 | 1 | U405 | D60V0L4B10LP | https://www.diodes.com/assets/Datasheets/D3V3XA4B10LP.pdf | D60V0L4B10LP-7 | https://www.digikey.com/en/products/detail/diodes-incorporated/D60V0L4B10LP-7/8550778 | $0.44 | $0.44
45 | 1 | R210 | 61.9k | https://www.te.com/commerce/DocumentDelivery/DDEController?Action=srchrtrv&DocNm=1773270&DocType=DS&DocLang=English | RN73C2A61K9BTDF | https://www.digikey.com/en/products/detail/te-connectivity-passive-product/RN73C2A61K9BTDF/2373785 | $1.09 | $1.09
46 | 2 | RN201, RN401 | 10k | https://www.vishay.com/docs/60045/tdp.pdf | TDPT16031002DUF | https://www.digikey.com/en/products/detail/vishay-dale-thin-film/TDPT16031002DUF/15183178 | $6.43 | $12.86
47 | 1 | R214 | Selected |  | Foil collector resistor |  | $30.00 | $30.00
48 | 1 | R213 | Selected |  | Foil anode resistor |  | $30.00 | $30.00
49 | 2 |  |  | https://www.switchcraft.com/assets/1/24/712A%20722A%20732A_CD.PDF?5243 | 712A | https://www.digikey.com/en/products/detail/switchcraft-inc/712A/109407 | $4.46 | $8.92
50 | 1 |  |  | https://www.switchcraft.com/assets/1/24/760K-765K_CD.PDF?5370 | 760K | https://www.digikey.com/en/products/detail/switchcraft-inc/760K/241922 | $6.62 | $6.62
51 | 1 |  |  | https://www.cuidevices.com/product/resource/md-pl100.pdf | MD-80PL100 | https://www.digikey.com/en/products/detail/cui-devices/MD-80PL100/500830 | $3.79 | $3.79
52 | 1 |  |  | https://app.adam-tech.com/products/download/data_sheet/199608/mdp-00x-data-sheet.pdf | MDP-008 | https://www.digikey.com/en/products/detail/adam-tech/MDP-008/10222603 | $1.69 | $1.69
53 | 1 |  |  | https://www.hammfg.com/electronics/small-case/extruded/1455.pdf | 1455N1601BK | https://www.digikey.com/en/products/detail/hammond-manufacturing/1455N1601BK/460178 | $32.18 | $32.18
54 | 1 |  |  | https://www.pomonaelectronics.com/file/17329/download?token=JnxIsd1L | 3770-0 | https://www.digikey.com/en/products/detail/pomona-electronics/3770-0/736559 | $12.99 | $12.99
55 | 1 |  |  | https://www.pomonaelectronics.com/file/17329/download?token=JnxIsd1L | 3770-2 | https://www.digikey.com/en/products/detail/pomona-electronics/3770-2/736561 | $12.99 | $12.99
56 | 1 |  | PCBs, Magnet Wire, Screws, Zip ties |  |  |  | $20.00 | $20.00
 |  |  | SUM |  |  |  |  | $370.77

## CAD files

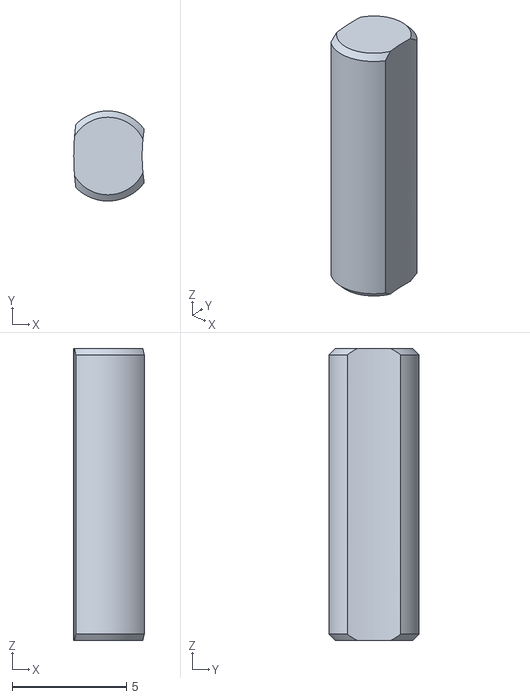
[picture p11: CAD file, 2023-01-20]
mechanical/3d/ADR_cap_top_SLA_2.stl
3.09 x 3.95 x 12.8

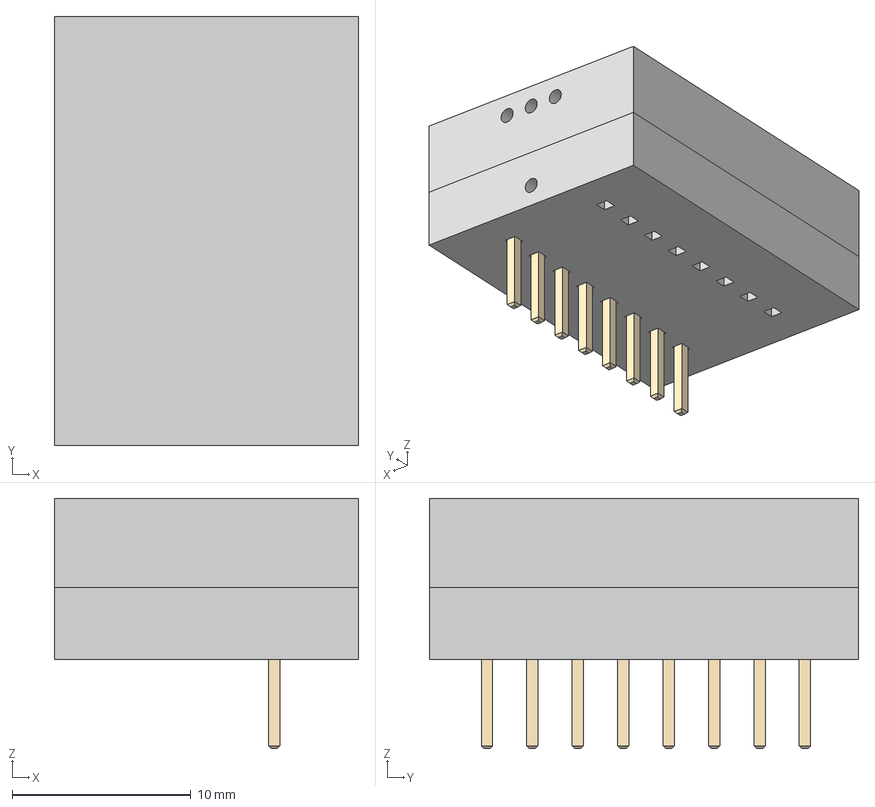
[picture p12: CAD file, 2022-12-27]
resistor_network/3d/resistor_network_shield.step
17.0 x 24.0 x 14.0 mm
resistor_network PCB

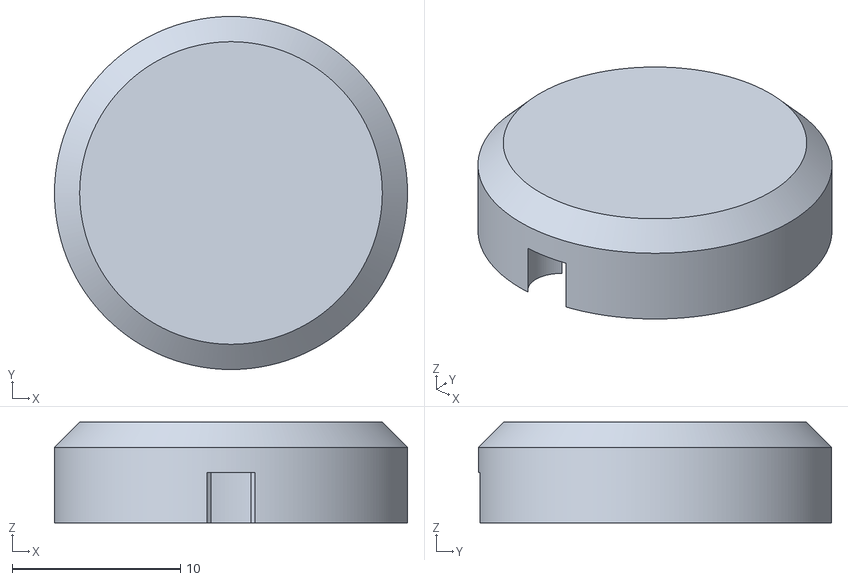
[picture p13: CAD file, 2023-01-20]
mechanical/3d/ADR_cap_bot_SLA_1.stl
21.0 x 21.0 x 6.00

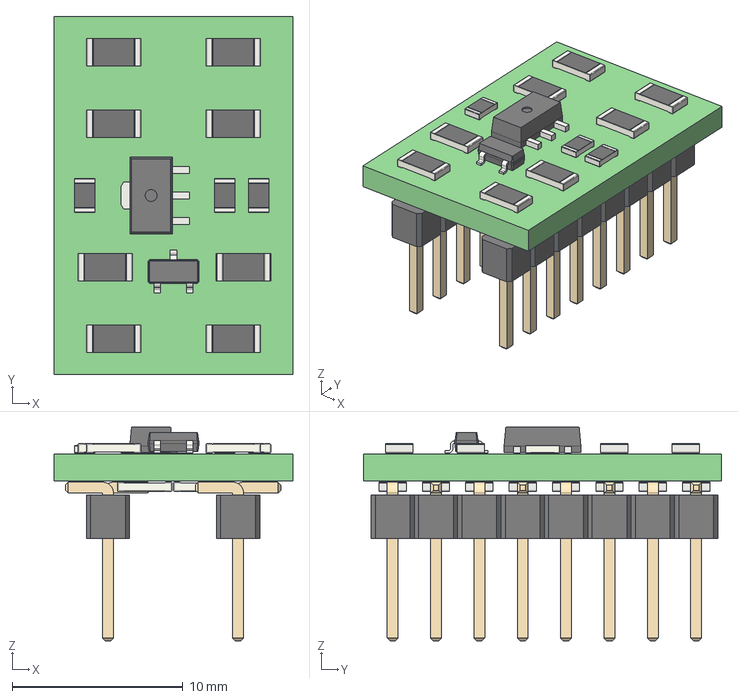
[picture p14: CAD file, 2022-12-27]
resistor_network/3d/resistor_network.step
14.0 x 21.0 x 12.5 mm
resistor_network PCB

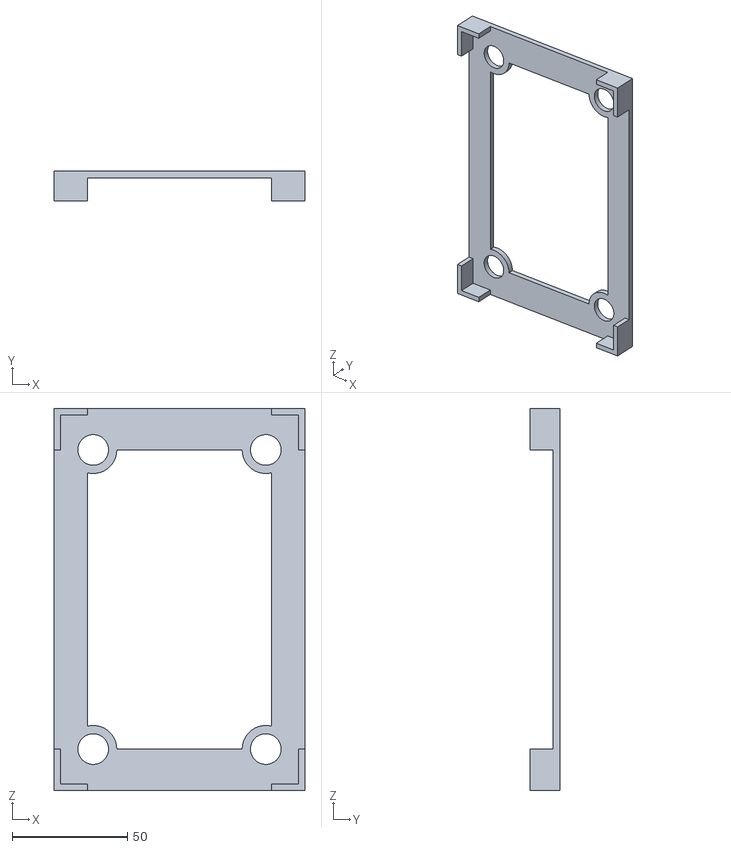
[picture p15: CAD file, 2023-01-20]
mechanical/3d/hammond_1455N1601BK_feet_positioner.stl
109.0 x 13.0 x 166.0

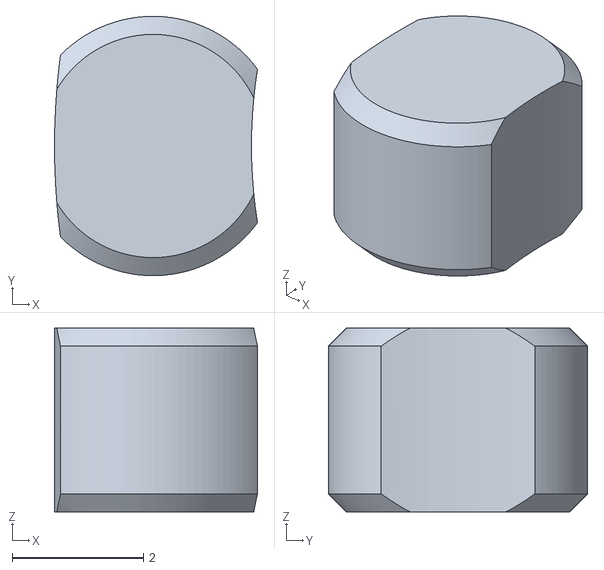
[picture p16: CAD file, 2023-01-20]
mechanical/3d/ADR_cap_bot_SLA_2.stl
3.09 x 3.95 x 2.80

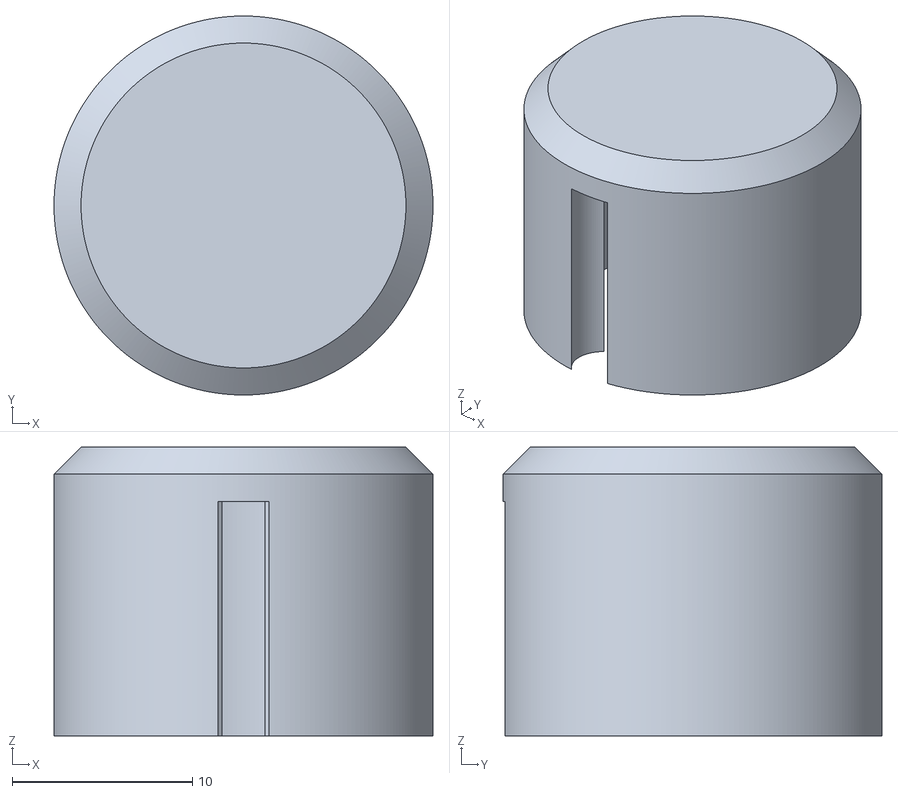
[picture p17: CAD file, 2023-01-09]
mechanical/3d/ADR_cap_top_SLA_1.stl
21.0 x 21.0 x 16.0

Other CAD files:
resistor_network/resistor_network.step

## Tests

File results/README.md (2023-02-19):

# ADRmu statistics
Click the .ipynb files, Github can display them!

# Low frequency noise
LFnoise measurements from Feb 2023 were made with a 0.1 ... 10 Hz noise preamp with x10000 gain. This is not accounted for in the oscilloscopes displayed values. Here's a frequency response analaysis of the preamp: https://github.com/RPG-Engineering/RSscope_scripts/blob/main/csv/euler_LNA_fra.ipynb

https://eulerprecision.com/

# ADR1000 theoretical noise
0.9 µVpp datasheet spec x 1.5 10V buffer gain x 10000 preamp gain
= 13.6 mVpp

# LTZ1000 theoretical noise
1.2 µVpp datasheet spec x 1.4 10V buffer gain x 10000 preamp gain
= 16.8 mVpp

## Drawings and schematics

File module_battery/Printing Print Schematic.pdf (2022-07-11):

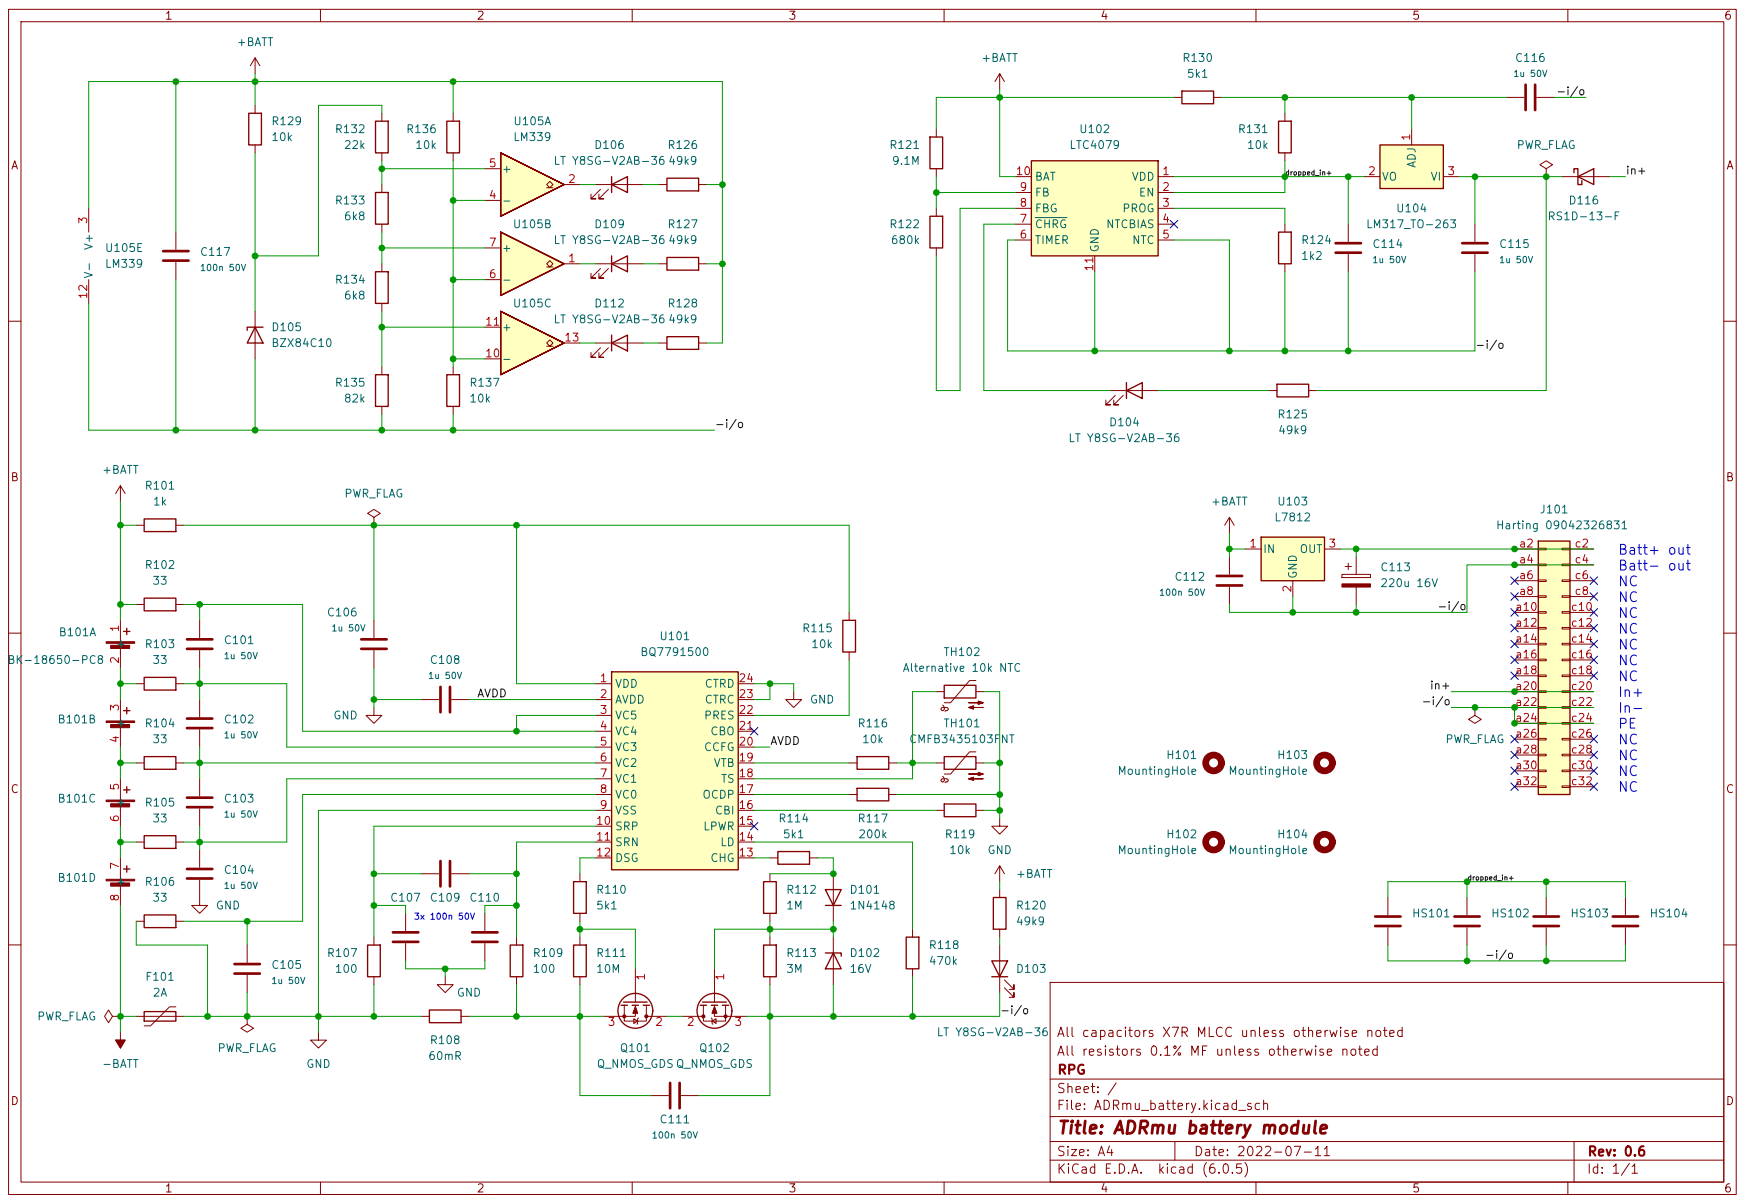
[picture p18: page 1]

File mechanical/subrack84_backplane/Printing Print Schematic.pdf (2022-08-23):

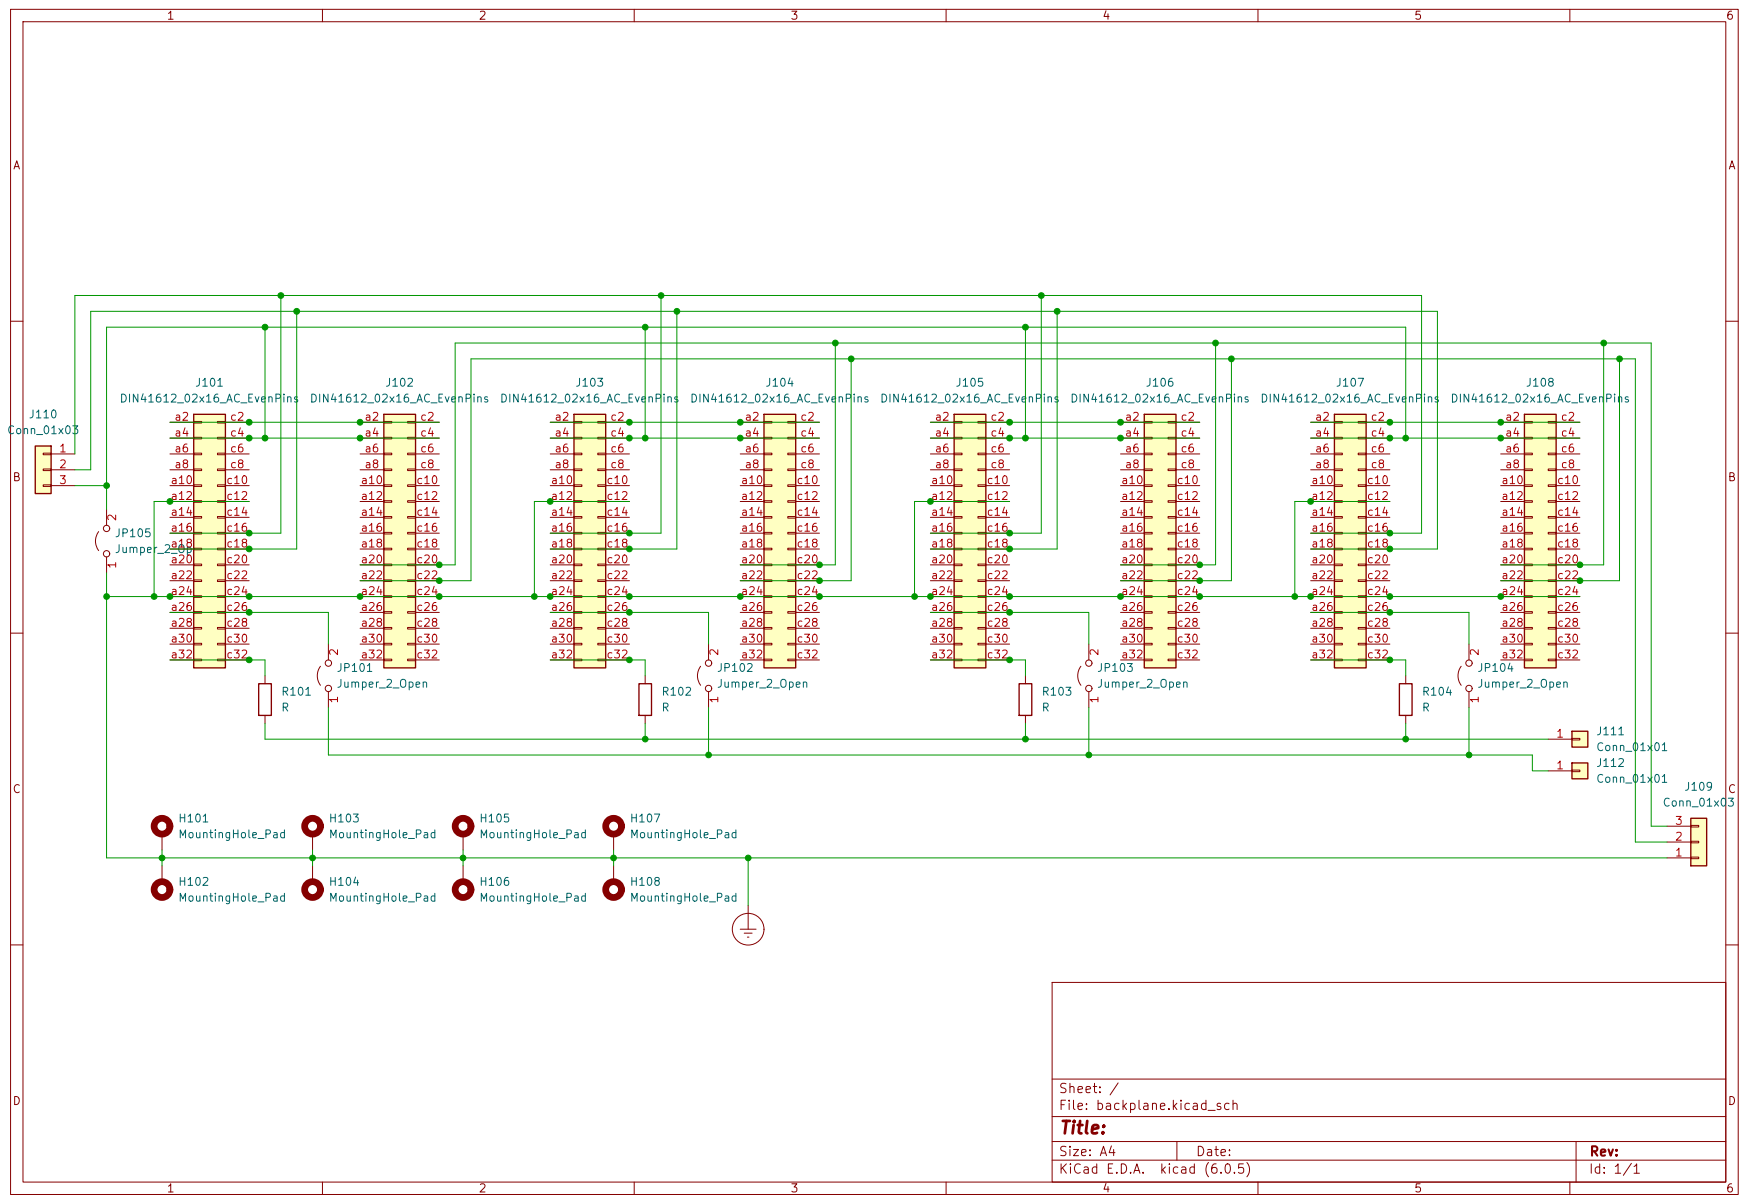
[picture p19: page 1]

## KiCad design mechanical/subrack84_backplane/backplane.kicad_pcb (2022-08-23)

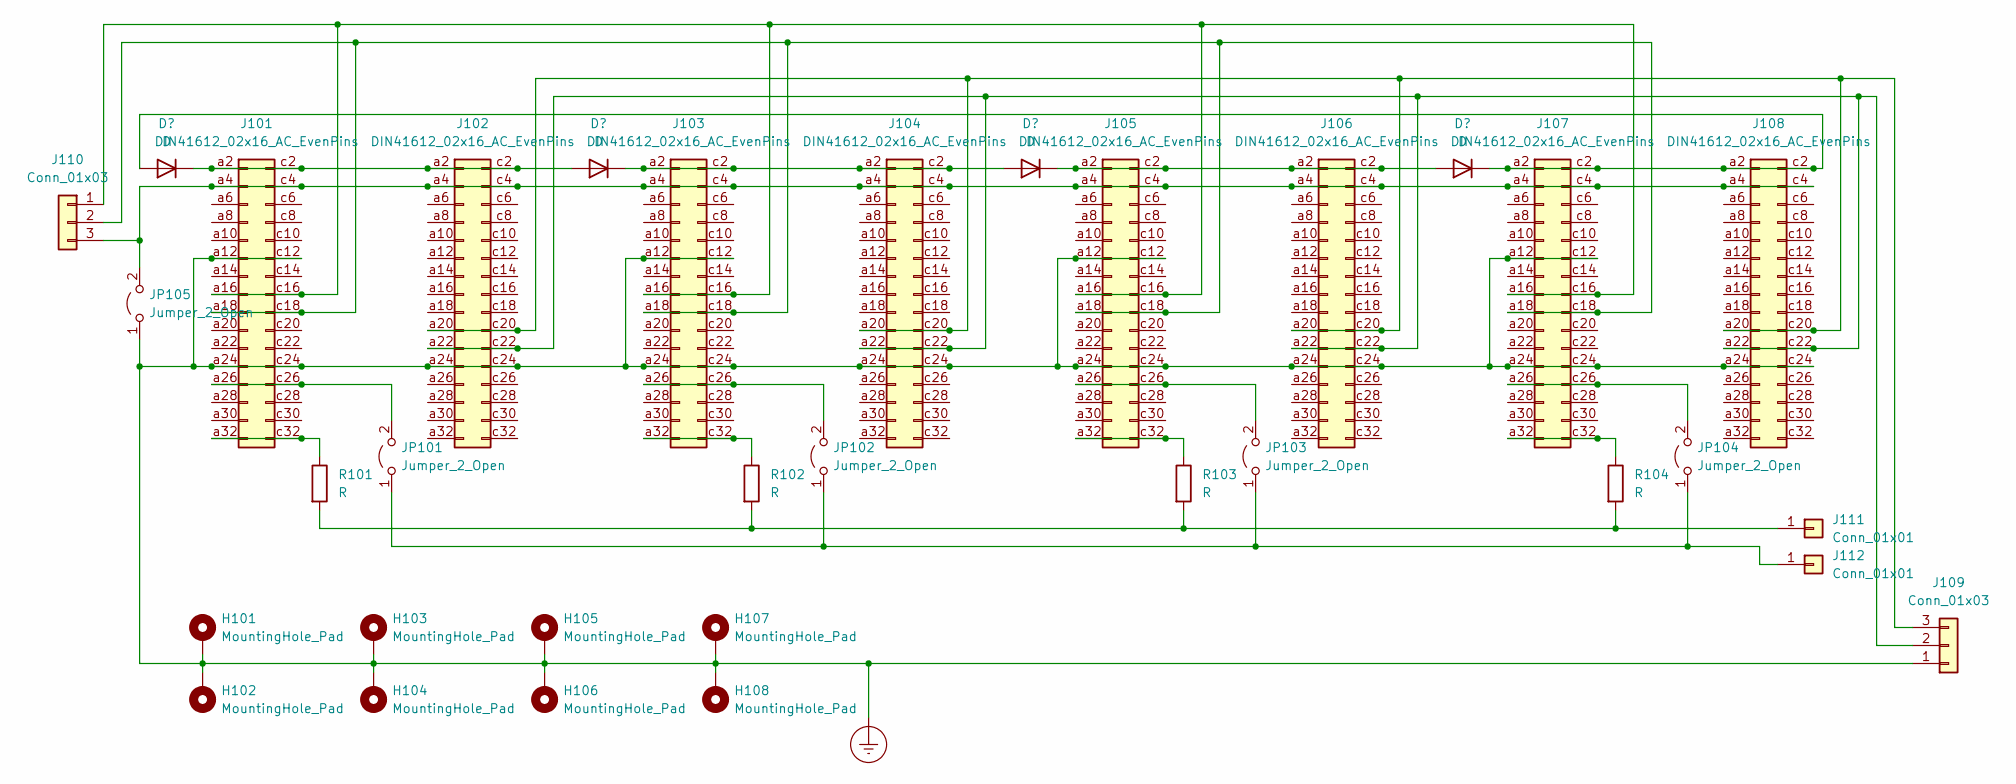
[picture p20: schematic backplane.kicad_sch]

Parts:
H101, H102, H103, H104, H105, H106, H107, H108: MountingHole_Pad; MountingHole_2.5mm_Pad
J101, J102, J103, J104, J105, J106, J107, J108: DIN41612_02x16_AC_EvenPins; DIN41612_C_2x16_Female_Vertical_THT
J109: Conn_01x03; TerminalBlock_WAGO_804-103_1x03_P5.00mm_45Degree
J110: Conn_01x03; JST_XH_B3B-XH-A_1x03_P2.50mm_Vertical
J111, J112: Conn_01x01; SolderWire-0.5sqmm_1x01_D0.9mm_OD2.1mm
JP101, JP102, JP103, JP104: Jumper_2_Open; SolderJumper-2_P1.3mm_Open_RoundedPad1.0x1.5mm
JP105: Jumper_2_Open; SolderJumper-2_P1.3mm_Bridged_RoundedPad1.0x1.5mm
R101, R102, R103, R104: R; R_0805_2012Metric

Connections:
Earth_Protective: H101.1, H102.1, H103.1, H104.1, H105.1, H106.1, H107.1, H108.1, J101.a12, J101.a24, J101.c12, J101.c24, J102.a24, J102.c24, J103.a12, J103.a24, J103.c12, J103.c24, J104.a24, J104.c24, J105.a12, J105.a24, J105.c12, J105.c24, J106.a24, J106.c24, J107.a12, J107.a24, J107.c12, J107.c24, J108.a24, J108.c24, J109.1, JP105.1 (A)
unnamed: J101.a2, J101.c2, J102.a2, J102.c2
unnamed: J101.a16, J101.c16, J103.a16, J103.c16, J105.a16, J105.c16, J107.a16, J107.c16, J110.1
unnamed: J101.a18, J101.c18, J103.a18, J103.c18, J105.a18, J105.c18, J107.a18, J107.c18, J110.2
unnamed: J101.a26, J101.c26, JP101.2 (B)
unnamed: J101.a32, J101.c32, R101.1
unnamed: J102.a20, J102.c20, J104.a20, J104.c20, J106.a20, J106.c20, J108.a20, J108.c20, J109.3
unnamed: J102.a22, J102.c22, J104.a22, J104.c22, J106.a22, J106.c22, J108.a22, J108.c22, J109.2
unnamed: J103.a2, J103.c2, J104.a2, J104.c2
unnamed: J103.a26, J103.c26, JP102.2 (B)
unnamed: J103.a32, J103.c32, R102.1
unnamed: J105.a2, J105.c2, J106.a2, J106.c2
unnamed: J105.a26, J105.c26, JP103.2 (B)
unnamed: J105.a32, J105.c32, R103.1
unnamed: J107.a2, J107.c2, J108.a2, J108.c2
unnamed: J107.a26, J107.c26, JP104.2 (B)
unnamed: J107.a32, J107.c32, R104.1
unnamed: J101.a4, J101.c4, J102.a4, J102.c4, J103.a4, J103.c4, J104.a4, J104.c4, J105.a4, J105.c4, J106.a4, J106.c4, J107.a4, J107.c4, J108.a4, J108.c4, J110.3, JP105.2 (B)
unnamed: J111.1, R101.2, R102.2, R103.2, R104.2
unnamed: J112.1, JP101.1 (A), JP102.1 (A), JP103.1 (A), JP104.1 (A)

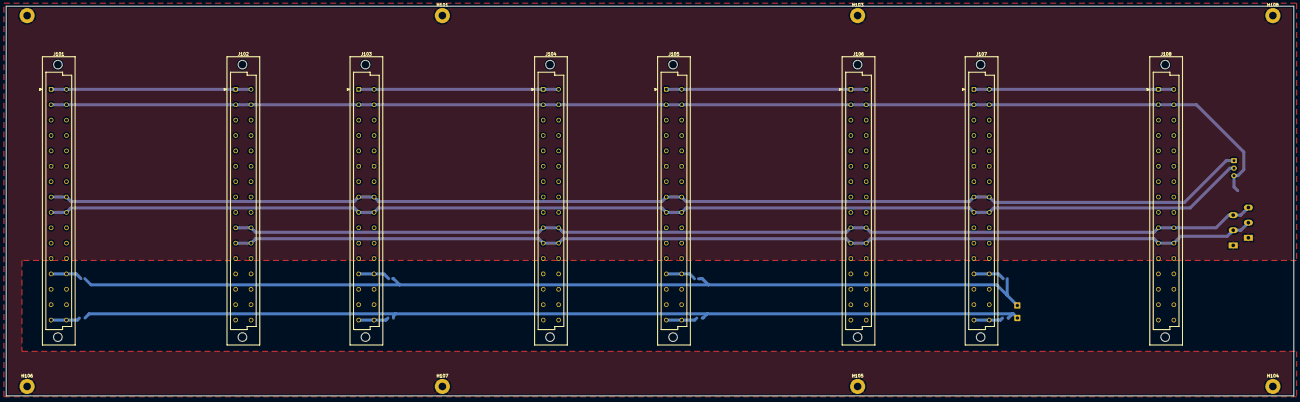
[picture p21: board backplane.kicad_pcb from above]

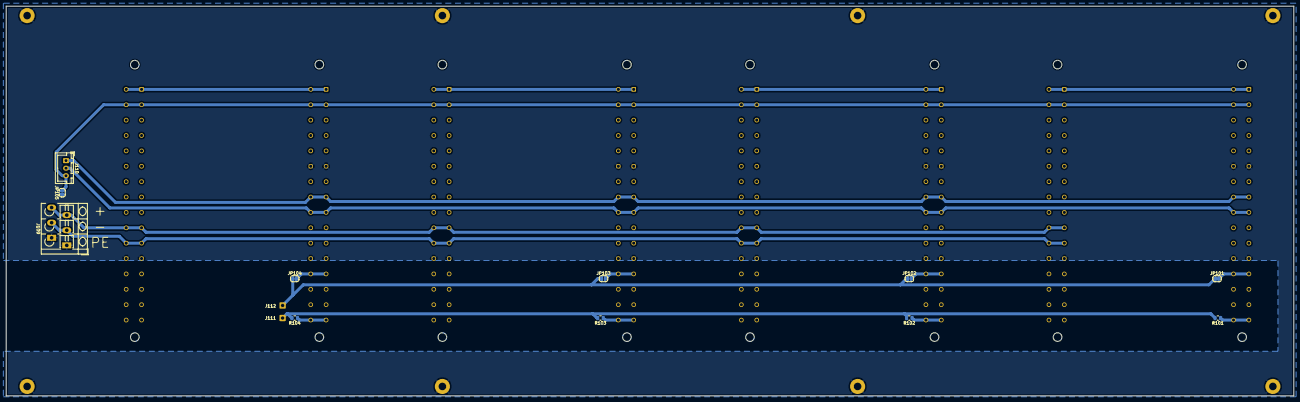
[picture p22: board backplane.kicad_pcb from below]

Board: 2 copper layers, 425.3 x 128.7 mm, 29 parts (13 on the bottom side), 20 nets.

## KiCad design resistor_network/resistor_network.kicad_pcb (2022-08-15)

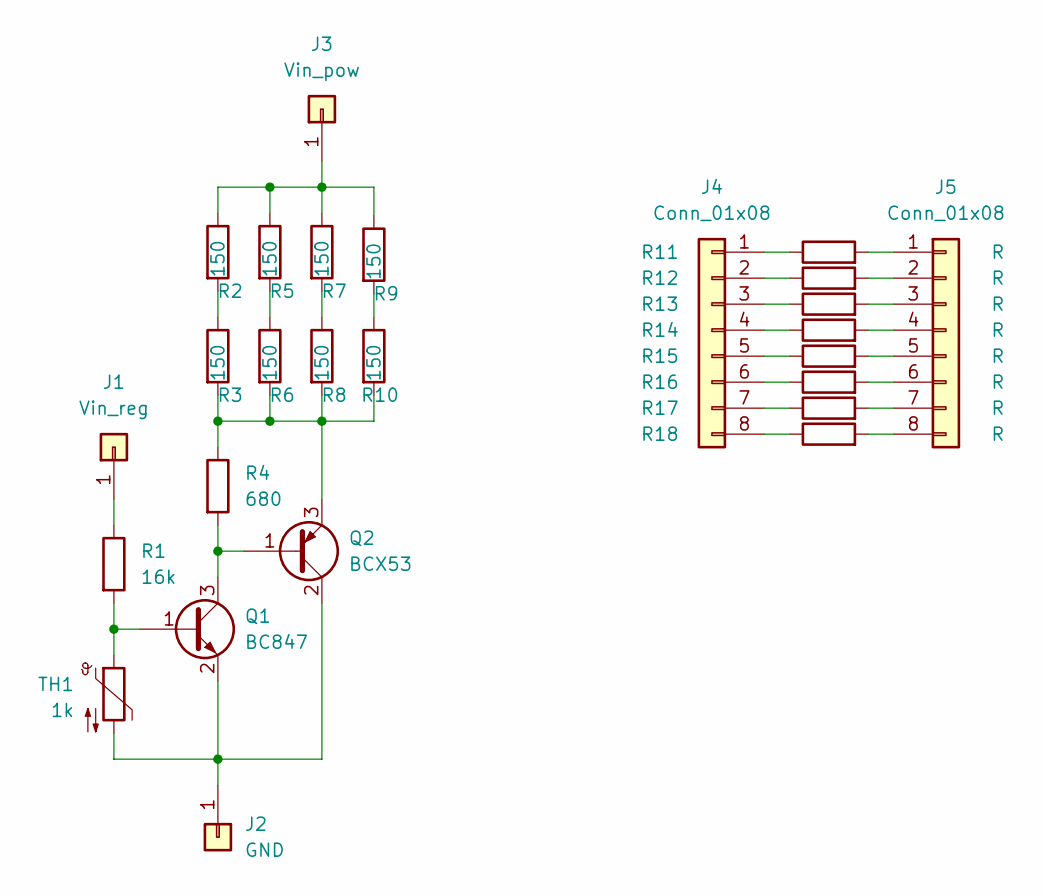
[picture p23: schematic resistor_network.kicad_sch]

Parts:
J1: Vin_reg; SolderWirePad_1x01_SMD_1x2mm
J2: GND; SolderWirePad_1x01_SMD_1x2mm
J3: Vin_pow; SolderWirePad_1x01_SMD_1x2mm
J4, J5: Conn_01x08; PinHeader_1x08_P2.54mm_Vertical_SMD_Pin1Left
Q1: BC847; SOT-23
Q2: BCX53; SOT-89-3
R1: 16k; R_0805_2012Metric
R2, R3, R5, R6, R7, R8, R9, R10: 150; R_1206_3216Metric
R4: 680; R_0805_2012Metric
R11, R12, R13, R14, R15, R16, R17, R18: R; R_1206_3216Metric
TH1: 1k; R_0805_2012Metric

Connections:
unnamed: J1.1, R1.1
unnamed: J2.1, Q1.2 (E), Q2.2 (C), TH1.2
unnamed: J3.1, R2.1, R5.1, R7.1, R9.1
unnamed: J4.1, R11.1
unnamed: J4.2, R12.1
unnamed: J4.3, R13.1
unnamed: J4.4, R14.1
unnamed: J4.5, R15.1
unnamed: J4.6, R16.1
unnamed: J4.7, R17.1
unnamed: J4.8, R18.1
unnamed: J5.1, R11.2
unnamed: J5.2, R12.2
unnamed: J5.3, R13.2
unnamed: J5.4, R14.2
unnamed: J5.5, R15.2
unnamed: J5.6, R16.2
unnamed: J5.7, R17.2
unnamed: J5.8, R18.2
unnamed: Q1.1 (B), R1.2, TH1.1
unnamed: Q1.3 (C), Q2.1 (B), R4.2
unnamed: Q2.3 (E), R3.2, R4.1, R6.2, R8.2, R10.2
unnamed: R2.2, R3.1
unnamed: R5.2, R6.1
unnamed: R7.2, R8.1
unnamed: R9.2, R10.1

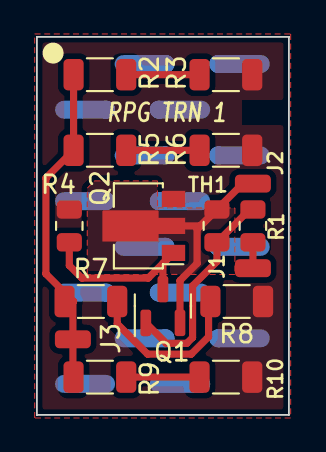
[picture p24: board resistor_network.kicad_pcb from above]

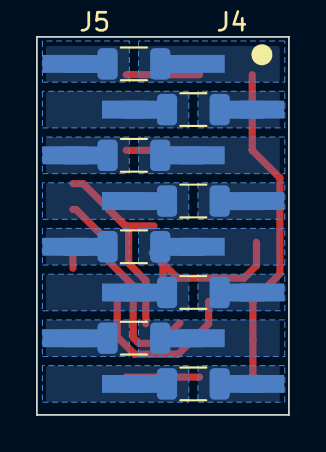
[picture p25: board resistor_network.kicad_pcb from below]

Board: 2 copper layers, 14.0 x 21.0 mm, 26 parts (10 on the bottom side), 26 nets.

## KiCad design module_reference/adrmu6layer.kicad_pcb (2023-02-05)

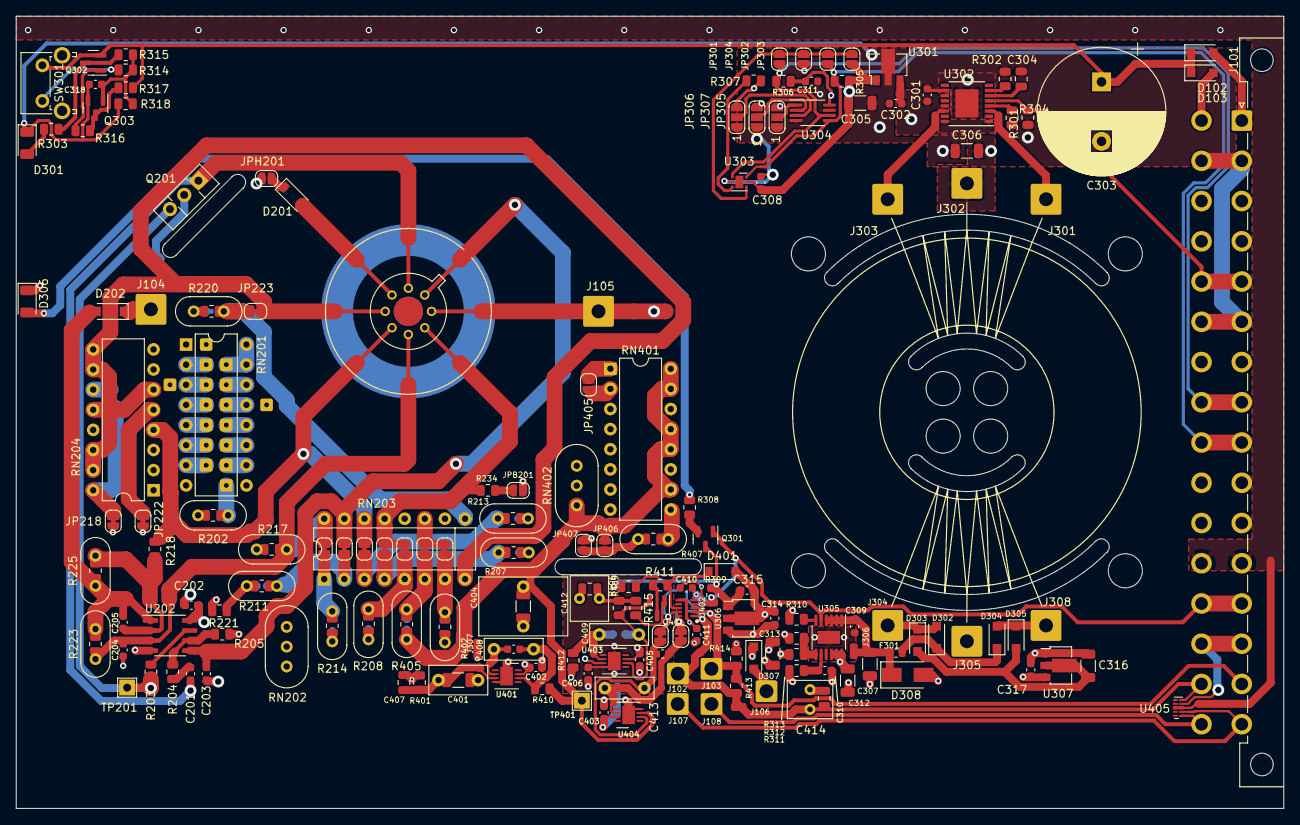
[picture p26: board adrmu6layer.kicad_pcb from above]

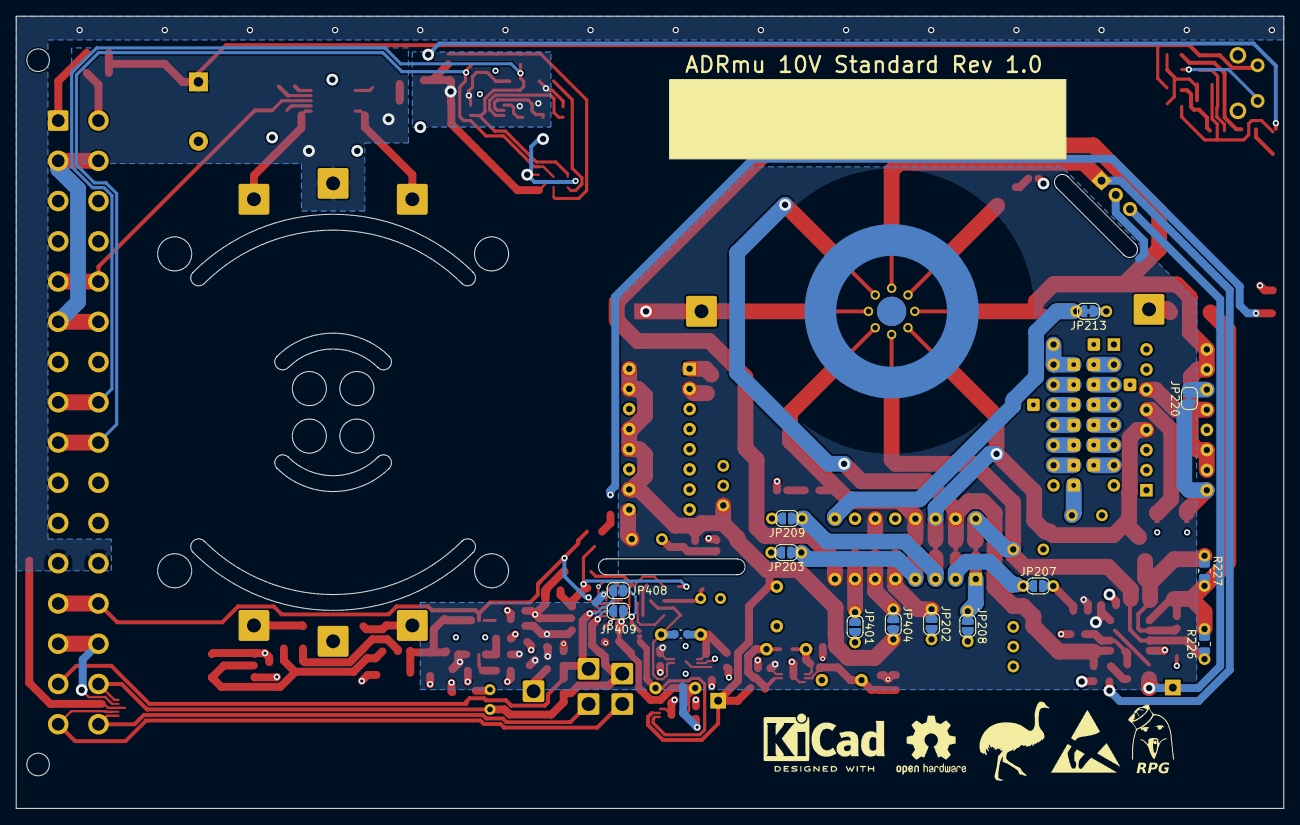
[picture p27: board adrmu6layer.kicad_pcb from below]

Board: 6 copper layers, 160.0 x 100.0 mm, 229 parts (19 on the bottom side), 101 nets.

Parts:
C201, C202, C203, C204, C205, C301, C302, C308, C309, C310, C311, C314, C315, C317, C318, C402, C403, C405, C406, C410, C411, C416, C417, C419: 100n 50V; C_0603_1608Metric
C303: 470u 25V; CP_Radial_D16.0mm_P7.50mm
C304: 1n 50V; C_0805_2012Metric
C305, C306, C307, C312, C313, C316, C418: 22u 25V; C_1206_3216Metric
C401: 470n Film; C_Rect_L7.2mm_W3.5mm_P5.00mm_FKS2_FKP2_MKS2_MKP2
C404: 10u Film; C_Rect_L7.2mm_W11.0mm_P5.00mm_FKS2_FKP2_MKS2_MKP2
C407: DNP; C_0805_2012Metric
C408, C409, C413: 100n Film; C_Rect_L7.2mm_W2.5mm_P5.00mm_FKS2_FKP2_MKS2_MKP2
C412, C414: 1u Film; C_Rect_L4.6mm_W5.5mm_P2.50mm_MKS02_FKP02
C415: 470n; C_1206_3216Metric
C420, C421: 1u; C_0805_2012Metric
D102, D103, D302, D303, D304, D305, D307: PMEG6010CEH; D_SOD-123F
D201, D202, D401: 1N4148; D_SOD-123
D301, D306: LT Y8SG-V2AB-36; LED_1206_3216Metric
D308: SMAJ15A-18; D_SMA
F301: SF-0603S040-2; Fuse_0603_1608Metric
H301, H302, H303, H304, H305, H306, H307, H308: MountingHole; MountingHole_4.3mm_M4
J101: Harting 09042326831; DIN41612_D_2x16_Male_Horizontal_THT
J102: OutHf; SolderWire-1sqmm_1x01_D1.4mm_OD2.7mm
J103: OutHs; SolderWire-1sqmm_1x01_D1.4mm_OD2.7mm
J104: 7Vref; SolderWire-1sqmm_1x01_D1.4mm_OD3.9mm
J105: Lo; SolderWire-1sqmm_1x01_D1.4mm_OD3.9mm
J106: 12VinC; SolderWire-1sqmm_1x01_D1.4mm_OD2.7mm
J107: OutLs; SolderWire-1sqmm_1x01_D1.4mm_OD2.7mm
J108: OutLf; SolderWire-1sqmm_1x01_D1.4mm_OD2.7mm
J201, J202, J203, J204, J205, J206, J207, J208, J209, J210, J211, J212, J214, J215, J216, J217: Conn_01x01; SolderWire-0.1sqmm_1x01_D0.4mm_OD1mm
J301, J302, J303, J304, J305, J308: Conn_01x01; SolderWire-1sqmm_1x01_D1.4mm_OD3.9mm
J306, J307, J401: Conn_01x01; SolderWirePad_1x01_SMD_1x2mm
JP202, JP203, JP207, JP208, JP209, JP301, JP302, JP303, JP304, JP401, JP404, JP405, JP406, JP407, JP408, JP409: Jumper_2_Open; SolderJumper-2_P1.3mm_Open_RoundedPad1.0x1.5mm
JP204, JP205, JP206, JP210, JP211, JP213, JP218, JP220, JP222, JP223, JP402, JP403, JP410, JP411: Jumper_2_Bridged; SolderJumper-2_P1.3mm_Bridged_RoundedPad1.0x1.5mm
JP305, JP306, JP307: Jumper_3_Open; SolderJumper-3_P1.3mm_Open_RoundedPad1.0x1.5mm_NumberLabels
JPB201: Jumper_2_Open; SolderJumper-2_P1.3mm_Open_RoundedPad1.0x1.5mm
JPH201: Jumper_2_Open; SolderJumper-2_P1.3mm_Open_RoundedPad1.0x1.5mm
NT201: NetTie_2; NetTie-2_SMD_Pad2.0mm
Q201: BD135; TO-126-3_Vertical
Q301, Q303, Q401: MMBT3904; SOT-23
Q302: MMBT3906; SOT-23
R201, R206, R209, R212, R215, R219, R403, R404: 0; R_0805_2012Metric
R202, R207, R208, R211, R213, R214, R220, R402, R405: 0; Crystal_HC52-U_Vertical
R203, R310, R401, R411, R412: 1k; R_0805_2012Metric
R204: 1M; R_0805_2012Metric
R205, R234, R301, R314, R315, R316, R317, R406, R415: 10k; R_0805_2012Metric
R210: 62k; R_0805_2012Metric
R216, R221, R318, R408, R413, R414: DNP; R_0805_2012Metric
R217, R407: DNP; Crystal_HC52-U_Vertical
R218: 30k; R_0805_2012Metric
R222, R224, R226, R227: TBD; R_0805_2012Metric
R223, R225: TBD; Crystal_HC52-U_Vertical
R302, R304: 16k9; R_0805_2012Metric
R303: 49.9k; R_0805_2012Metric
R305, R306, R307: 4k99; R_0805_2012Metric
R308: 2k7; R_0805_2012Metric
R309: 200k; R_0805_2012Metric
R311: 130k; R_0805_2012Metric
R312: 750k; R_0805_2012Metric
R313: 18k; R_0805_2012Metric
R409: 62; R_0805_2012Metric
R410: 47; R_0805_2012Metric
RN201, RN401: Vishay TDP 10k; DIP-16_W7.62mm
RN202, RN402: DNP; Resonator-3Pin_W10.0mm_H5.0mm
RN203: 322146+1; VPG322146+1
RN204: Vishay TDP 100; DIP-16_W7.62mm
SW301: SW_Push; SW_Tactile_SPST_Angled_PTS645Vx31-2LFS
SYM101: OSMU; osmu_logo
SYM102: SYM_ESD_Small; ESD-Logo_8.9x8mm_SilkScreen
SYM103: Logo_Open_Hardware_Small; OSHW-Logo2_9.8x8mm_SilkScreen
SYM104: Logo_Open_Hardware_Small; KiCad-Logo2_6mm_SilkScreen
SYM105: Logo_Open_Hardware_Small; moin_logo
TP201, TP401: TestPoint; TestPoint_THTPad_2.0x2.0mm_Drill1.0mm
U201: ADR1000; TO-5-8
U202: OPA2172; SOIC-8_3.9x4.9mm_P1.27mm
U301, U306: L78L33_SOT89; SOT-89-3
U302: LT3439; TSSOP-16-1EP_4.4x5mm_P0.65mm
U303: TMP117; WSON-6-1EP_2x2mm_P0.65mm_EP1x1.6mm
U304: BR24H64FVM; MSOP-8_3x3mm_P0.65mm
U305: LT3045xMSE; MSOP-12-1EP_3x4mm_P0.65mm_EP1.65x2.85mm
U307: L79L05_SOT89; SOT-89-3
U401, U403, U404: ADA4523; LFCSP-8-1EP_3x3mm_P0.5mm_EP1.6x2.34mm
U402: ADG5401F; LFCSP-10
U405: D60V0L4B10LP; Diodes_UDFN-10_1.0x2.5mm_P0.5mm

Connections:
+3V3: C305.1, C308.1, C311.1, JP303.1 (A), JP305.3 (B), JP306.3 (B), JP307.3 (B), R305.1, R306.1, R307.1, U301.1 (OUT), U303.5 (V+), U304.8 (VCC)
+12V: C301.1, C302.1, C303.1, C306.1, D102.1 (K), D103.1 (K), J302.1, Q302.2 (E), R317.1, SW301.2, U301.3 (IN), U302.11 (~SHDN), U302.13 (VIN)
/Buffer/3Vf: C315.1, Q301.3 (C), R309.2, R406.2, U306.1 (OUT)
/Buffer/12Vf: C202.2, C312.1, C313.1, C314.1, C402.2, C403.2, C405.2, C410.2, D307.1 (K), Q201.2 (C), R221.2, R312.1, U202.8 (V+), U305.10 (OUTS), U305.11 (OUT), U305.12 (OUT), U306.3 (IN), U401.7 (V+), U402.5 (VDD), U403.7 (V+), U404.7 (V+)
/Buffer/-5Vf: C317.2, C406.1, C411.2, U307.3 (VO), U402.6 (VSS), U403.4 (V-), U403.9 (V-)
/Buffer/ADR_Pin7: C203.1, C204.1, C401.1, C415.2, J105.1, J215.1, J216.1, JP203.2 (B), JP209.2 (B), JP401.2 (B), JP407.1 (A), JPB201.2 (B), NT201.2, R207.2, R209.2, R213.2, R215.2, R402.2, R403.2, R414.1, RN201.9 (8..2), RN202.3, RN204.13 (R4.2), RN401.11 (R6.2), RN401.14 (R3.2), RN402.3, U201.7 (GND), U403.3 (+)
/Buffer/FF: J101.a26, J101.c26, Q301.1 (B), R309.1, U305.5 (PG), U402.3 (FF)
/Buffer/GNDf: C202.1, C307.2, C309.2, C310.2, C312.2, C313.2, C314.2, C315.2, C316.1, C317.1, C402.1, C403.1, C404.2, C405.1, C406.2, C410.1, C411.1, C412.2, C414.2, C418.2, C420.2, C421.2, D306.1 (K), D308.2 (A), D401.2 (A), J101.a28, J101.c28, J305.1, J307.1, JPH201.2 (B), NT201.1, R310.2, R311.2, R313.2, U202.4 (V-), U305.9 (GND), U305.13 (GND), U306.2 (GND), U307.1 (GND), U401.4 (V-), U401.9 (V-), U402.4 (GND), U404.4 (V-), U404.9 (V-), U405.4
/Buffer/JP404_pin2: C404.1, C418.1, JP404.2 (B), JP406.1 (A), R404.2, R405.2, R410.1, RN401.10 (R7.2), RN401.12 (R5.2), RN401.13 (R4.2), RN401.15 (R2.2), RN401.16 (1.2), RN402.1, TP401.1, U404.3 (+)
/Buffer/JP406_Pin2: JP406.2 (B), JP407.2 (B), R407.1, R408.1
/Buffer/OutHf: C414.1, C421.1, J101.c30, J102.1, J401.1, JP409.2 (B), R413.2, U402.1 (S), U405.5
/Buffer/OutHs: J101.a30, J103.1, JP408.1 (A), R413.1, R414.2, U402.2 (SFB)
/Buffer/OutLf: C412.1, C420.1, J101.c32, J108.1, R409.2, R415.1, U405.1
/Buffer/OutLs: J101.a32, J107.1, R412.1, U405.2
/Buffer/RN203_Pin6: JP403.1 (A), JP404.1 (A), R404.1, R405.1, RN203.6 (R6.1)
/Buffer/RN203_Pin7: JP401.1 (A), JP402.2 (B), R402.1, R403.1, RN203.7 (R7.1)
/Buffer/RN401_Pin1: JP405.2 (B), RN401.1 (1.1)
/Buffer/RN401_Pin9: R407.2, R408.2, RN401.9 (8..2)
/Buffer/U401_+in: C401.2, C407.1, C415.1, R401.1, U401.3 (+)
/Buffer/U401_-in: C408.2, C416.2, JP402.1 (A), JP403.2 (B), JP405.1 (A), RN203.10 (R7.2), RN401.2 (R2.1), RN401.3 (R3.1), RN401.4 (R4.1), RN401.5 (R5.1), RN401.6 (R6.1), RN401.7 (R7.1), RN401.8 (1.1), RN402.2, U401.2 (-)
/Buffer/U401_out: C408.1, C416.1, R410.2, U401.6
/Buffer/U402_D: JP409.1 (A), JP410.2 (B), U402.10 (D)
/Buffer/U402_DFB: JP408.2 (B), JP411.2 (B), U402.9 (DFB)
/Buffer/U402_in: D401.1 (K), R406.1, R411.2, U402.8 (IN)
/Buffer/U403_-in: C409.2, C417.2, R412.2, U403.2 (-)
/Buffer/U403_out: C409.1, C417.1, Q401.2 (E), R409.1, U403.6
/Buffer/U404_-in: C413.2, C419.2, JP411.1 (A), U404.2 (-)
/Buffer/U404_out: C413.1, C419.1, JP410.1 (A), U404.6
/DC-DC converter/+12VinA: D102.2 (A), J101.a2
/DC-DC converter/+12VinB: D103.2 (A), J101.c2
/DC-DC converter/+12VinC: D307.2 (A), J106.1
/DC-DC converter/D301_A: D301.2 (A), R303.1
/DC-DC converter/D306_A: D306.2 (A), R308.2
/DC-DC converter/Q301_e: Q301.2 (E), R308.1
/DC-DC converter/Q302_b: Q302.1 (B), R316.2
/DC-DC converter/Q302_c: Q302.3 (C), R303.2, R315.2
/DC-DC converter/Q303_b: C318.1, Q303.1 (B), R314.2, R315.1, R318.2
/DC-DC converter/Q303_c: Q303.3 (C), R316.1, R317.2
/DC-DC converter/SCL: J101.a16, J101.c16, JP301.1 (A), R306.2, U303.1 (SCL), U304.6 (SCL)
/DC-DC converter/SDA: J101.a18, J101.c18, JP302.1 (A), R305.2, U303.6 (SDA), U304.5 (SDA)
/DC-DC converter/SW301: R314.1, SW301.1
/DC-DC converter/U302_cola: J301.1, U302.3 (COLA)
/DC-DC converter/U302_colb: J303.1, U302.14 (COLB)
/DC-DC converter/U302_ct: C304.1, U302.6 (Ct)
/DC-DC converter/U302_rsl: R304.1, U302.4 (Rsl)
/DC-DC converter/U302_rt: R302.1, U302.7 (Rt)
/DC-DC converter/U303_add0: JP301.2 (B), JP302.2 (B), JP303.2 (B), JP304.2 (B), U303.4 (ADD0)
/DC-DC converter/U303_alert: R307.2, U303.3 (ALERT)
/DC-DC converter/U304_a0: JP305.2 (C), U304.1 (A0)
/DC-DC converter/U304_a1: JP307.2 (C), U304.2 (A1)
/DC-DC converter/U304_a2: JP306.2 (C), U304.3 (A2)
/DC-DC converter/U305_ilim: R310.1, U305.6 (ILIM)
/DC-DC converter/U305_in: C307.1, C309.1, D308.1 (K), F301.2, J306.1, U305.1 (IN), U305.2 (IN), U305.3 (IN), U305.4 (EN/UV)
/DC-DC converter/U305_pgfb: R312.2, R313.1, U305.7 (PGFB)
/DC-DC converter/U305_set: C310.1, R311.1, U305.8 (SET)
/DC-DC converter/U307_vi: C316.2, D303.2 (A), D305.2 (A), U307.2 (VI)
/DC-DC converter/rectified+: D302.1 (K), D304.1 (K), F301.1
/DC-DC converter/sync: J101.a10, J101.c10, R301.1, U302.5 (SYNC)
/DC-DC converter/xformer_A: D302.2 (A), D303.1 (K), J304.1
/DC-DC converter/xformer_B: D304.2 (A), D305.1 (K), J308.1
/Reference Circuit/7Vref: C407.2, D202.1 (K), J104.1, J214.1, JP202.2 (B), JP207.2 (B), JP208.2 (B), JP213.1 (A), JP218.1 (A), JP222.1 (A), R206.2, R208.2, R210.2, R211.2, R212.2, R214.2, R216.2, R217.2, R219.2, R220.2, R221.1, R401.2, RN201.1 (1.1), RN202.1, RN204.1 (1.1), RN204.2 (R2.1), RN204.3 (R3.1), RN204.7 (R7.1), RN204.8 (1.1)
/Reference Circuit/ADR_Pin3: JP223.2 (B), RN203.8 (1.1), RN204.6 (R6.1), RN204.9 (8..2), RN204.10 (R7.2), RN204.12 (R5.2), RN204.14 (R3.2), RN204.15 (R2.2), U201.3 (VREF)
/Reference Circuit/ADR_Pin4: JP211.2 (B), R218.1, RN203.12 (R3.2), RN204.4 (R4.1), U201.4 (IZSET)
/Reference Circuit/ADR_Pin5: C204.2, JP210.2 (B), R216.1, R217.1, R222.1, R223.2, R226.1, RN203.14 (1.2), U201.5 (CQ1), U202.3 (+)
/Reference Circuit/ADR_Pin6: J217.1, JP204.2 (B), JP205.1 (A), R201.1, R202.1, R205.1, R234.2, RN201.7 (R7.1), RN201.8 (1.1), RN202.2, RN203.11 (R5.2), U201.6 (BQ2)
/Reference Circuit/ADR_Pin8: C203.2, JP206.2 (B), RN203.13 (R2.2), U201.8 (CQ2), U202.5 (+)
/Reference Circuit/J213_Pin1: JP213.2 (B), JP223.1 (A), R219.1, R220.1, RN203.9 (8..2)
/Reference Circuit/JP201_Pin1: J203.1, R201.2, R202.2
/Reference Circuit/JPB_Pin1: JPB201.1 (A), R234.1
/Reference Circuit/JPH_Pin1: D201.1 (K), JPH201.1 (A)
/Reference Circuit/Q201_base: Q201.3 (B), R203.1, TP201.1
/Reference Circuit/R204_Pin1: C201.2, R204.1
/Reference Circuit/RN201_Pin2: J204.1, RN201.2 (R2.1)
/Reference Circuit/RN201_Pin3: J205.1, RN201.3 (R3.1)
/Reference Circuit/RN201_Pin4: J202.1, RN201.4 (R4.1)
/Reference Circuit/RN201_Pin5: J211.1, RN201.5 (R5.1)
/Reference Circuit/RN201_Pin6: J212.1, RN201.6 (R6.1)
/Reference Circuit/RN201_Pin10: J209.1, RN201.10 (R7.2)
/Reference Circuit/RN201_Pin11: J208.1, RN201.11 (R6.2)
/Reference Circuit/RN201_Pin12: J207.1, RN201.12 (R5.2)
/Reference Circuit/RN201_Pin13: J206.1, RN201.13 (R4.2)
/Reference Circuit/RN201_Pin14: J201.1, RN201.14 (R3.2)
/Reference Circuit/RN201_Pin15: J210.1, RN201.15 (R2.2), RN201.16 (1.2)
/Reference Circuit/RN203_Pin1: JP208.1 (A), JP210.1 (A), R212.1, R214.1, RN203.1 (1.1)
/Reference Circuit/RN203_Pin2: JP206.1 (A), JP207.1 (A), R210.1, R211.1, RN203.2 (R2.1)
/Reference Circuit/RN203_Pin3: JP209.1 (A), JP211.1 (A), R213.1, R215.1, RN203.3 (R3.1)
/Reference Circuit/RN203_Pin4: JP203.1 (A), JP205.2 (B), R207.1, R209.1, RN203.4 (R4.1)
/Reference Circuit/RN203_Pin5: JP202.1 (A), JP204.1 (A), R206.1, R208.1, RN203.5 (R5.1)
/Reference Circuit/RN204_Pin5: JP222.2 (B), RN204.5 (R5.1)
/Reference Circuit/RN204_Pin11: JP220.2 (B), RN204.11 (R6.2)
/Reference Circuit/RN204_Pin16: JP218.2 (B), JP220.1 (A), RN204.16 (1.2)
/Reference Circuit/U202A_-in: C205.2, R218.2, R224.1, R225.2, R227.1, U202.2 (-)
/Reference Circuit/U202A_out: C205.1, D202.2 (A), R222.2, R223.1, R224.2, R225.1, R226.2, R227.2, U202.1
/Reference Circuit/U202B_-in: R204.2, R205.2, U202.6 (-)
/Reference Circuit/U202B_out: R203.2, U202.7
/Reference Circuit/heater+: C201.1, Q201.1 (E), U201.1 (HTR+)
/Reference Circuit/heater-: D201.2 (A), U201.2 (HTR-)
Earth: J101.a24, J101.c24, U405.3 (VSS), U405.8 (VSS)
GND: C301.2, C302.2, C303.2, C304.2, C305.2, C306.2, C308.2, C311.2, C318.2, D301.1 (K), J101.a4, J101.a12, J101.c4, J101.c12, JP304.1 (A), JP305.1 (A), JP306.1 (A), JP307.1 (A), Q303.2 (E), R301.2, R302.2, R304.2, R318.1, U301.2 (GND), U302.1 (PGND), U302.10 (GND), U302.16 (PGND), U302.17 (PADGND), U303.2 (GND), U304.4 (GND), U304.7 (WP)
unnamed: Q401.1 (B), R415.2
unnamed: Q401.3 (C), R411.1

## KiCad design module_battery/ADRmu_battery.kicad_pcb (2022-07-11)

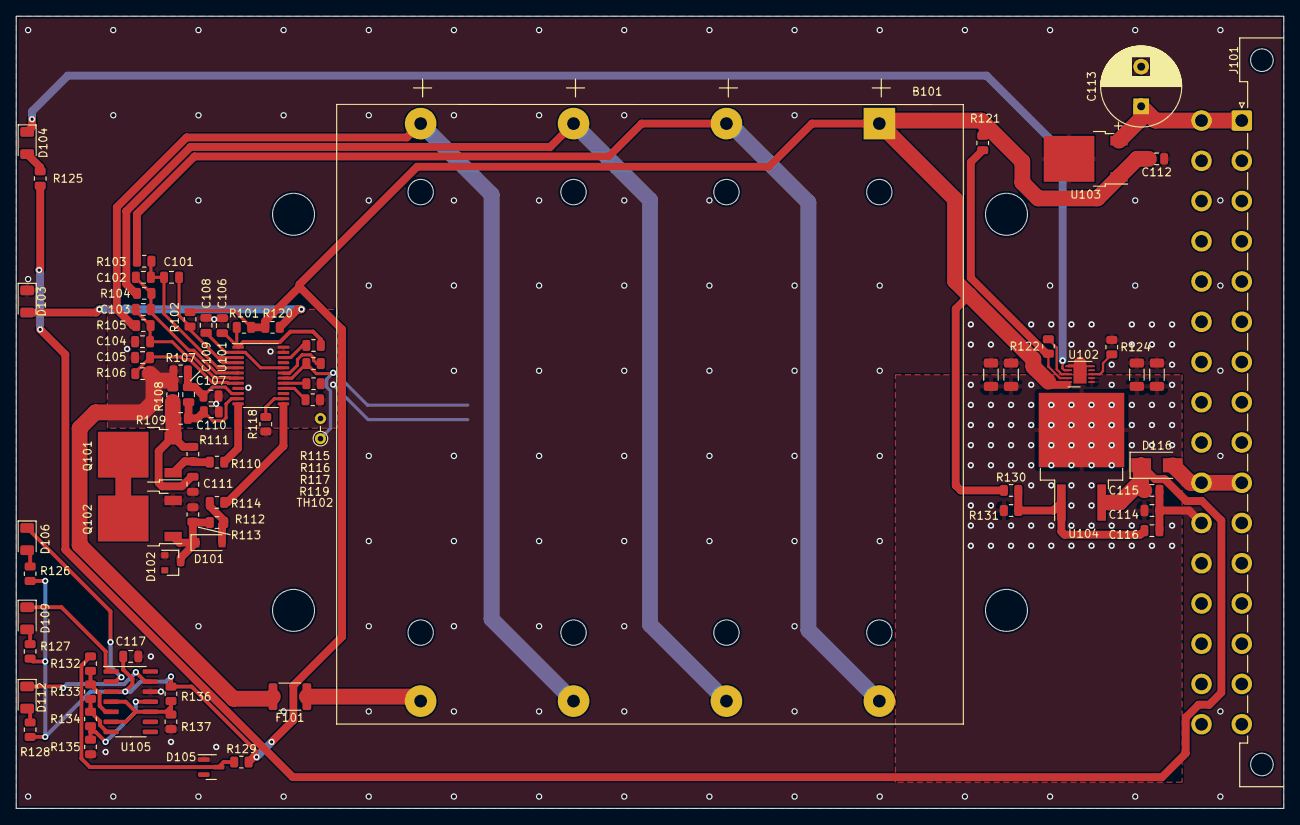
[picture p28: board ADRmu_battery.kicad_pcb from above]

Board: 2 copper layers, 160.0 x 100.0 mm, 82 parts (1 on the bottom side), 51 nets.

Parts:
B101: BK-18650-PC8
C101, C102, C103, C104, C105, C106, C108, C114, C115, C116: 1u 50V; C_0805_2012Metric
C107, C109, C110, C111, C112, C117: 100n 50V; C_0805_2012Metric
C113: 220u 16V; CP_Radial_D10.0mm_P5.00mm
D101: 1N4148; D_SOD-123
D102: 16V; D_SOT-23_ANK
D103, D104, D106, D109, D112: LT Y8SG-V2AB-36; LED_1206_3216Metric
D105: BZX84C10; SOT-23
D116: RS1D-13-F; D_SMA
F101: 2A; Fuse_1812_4532Metric
H101, H102, H103, H104: MountingHole; MountingHole_5.3mm_M5
HS101, HS102, HS103, HS104: THJP1206AST1; C_1206_3216Metric
J101: Harting 09042326831; DIN41612_D_2x16_Male_Horizontal_THT
Q101, Q102: Q_NMOS_GDS; TO-252-2
R101: 1k; R_0805_2012Metric
R102, R103, R104, R105, R106: 33; R_0805_2012Metric
R107, R109: 100; R_0805_2012Metric
R108: 60mR; R_0805_2012Metric
R110, R114, R130: 5k1; R_0805_2012Metric
R111: 10M; R_0805_2012Metric
R112: 1M; R_0805_2012Metric
R113: 3M; R_0805_2012Metric
R115, R116, R119, R129, R131, R136, R137: 10k; R_0805_2012Metric
R117: 200k; R_0805_2012Metric
R118: 470k; R_0805_2012Metric
R120, R125, R126, R127, R128: 49k9; R_0805_2012Metric
R121: 9.1M; R_0805_2012Metric
R122: 680k; R_0805_2012Metric
R124: 1k2; R_0805_2012Metric
R132: 22k; R_0805_2012Metric
R133, R134: 6k8; R_0805_2012Metric
R135: 82k; R_0805_2012Metric
TH101: CMFB3435103FNT; R_0805_2012Metric
TH102: Alternative 10k NTC; R_Axial_DIN0204_L3.6mm_D1.6mm_P2.54mm_Vertical
U101: BQ7791500; TSSOP-24_4.4x7.8mm_P0.65mm
U102: LTC4079; DFN-10-1EP_3x3mm_P0.5mm_EP1.65x2.38mm
U103: L7812; TO-252-2
U104: LM317_TO-263; TO-263-2
U105: LM339; SOIC-14_3.9x8.7mm_P1.27mm

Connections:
+BATT: B101.1 (+), C112.2, C117.2, R101.1, R102.1, R120.1, R121.2, R126.2, R127.2, R128.2, R129.2, R130.2, R136.2, U102.10 (BAT), U103.1 (IN), U105.3 (V+)
-BATT: B101.8 (-), F101.1
/-i/o: C111.2, C112.1, C113.2, C114.2, C115.2, C116.2, C117.1, D102.2 (A), D103.1 (K), D105.1 (A), HS101.2, HS102.2, HS103.2, HS104.2, J101.a4, J101.a22, J101.a24, J101.c4, J101.c22, J101.c24, Q102.3 (S), R113.1, R118.1, R124.1, R135.1, R137.1, U102.5 (NTC), U102.6 (TIMER), U102.11 (GND), U103.2 (GND), U105.12 (V-)
/AVDD: C108.2, U101.2 (AVDD), U101.20 (CCFG)
/dropped_in+: C114.1, HS101.1, HS102.1, HS103.1, HS104.1, R131.1, U102.1 (VDD), U102.2 (EN), U104.2 (VO)
/in+: D116.2 (A), J101.a20, J101.c20
GND: C104.2, C105.2, C106.2, C107.1, C108.1, C110.1, F101.2, R106.1, R107.1, R108.1, R117.1, R119.1, TH101.2, TH102.2, U101.9 (VSS), U101.23 (CTRC), U101.24 (CTRD)
unnamed: B101.2 (-), B101.3 (+), R103.1
unnamed: B101.4 (-), B101.5 (+), R104.1
unnamed: B101.6 (-), B101.7 (+), R105.1
unnamed: C101.1, R102.2, U101.3 (VC5), U101.4 (VC4)
unnamed: C101.2, C102.1, R103.2, U101.5 (VC3)
unnamed: C102.2, C103.1, R104.2, U101.6 (VC2)
unnamed: C103.2, C104.1, R105.2, U101.7 (VC1)
unnamed: C105.1, R106.2, U101.8 (VC0)
unnamed: C106.1, R101.2, R115.2, U101.1 (VDD)
unnamed: C107.2, C109.1, R107.2, U101.10 (SRP)
unnamed: C109.2, C110.2, R109.2, U101.11 (SRN)
unnamed: C111.1, Q101.3 (S), R108.2, R109.1, R111.1
unnamed: C113.1, J101.a2, J101.c2, U103.3 (OUT)
unnamed: C115.1, D116.1 (K), R125.1, U104.3 (VI)
unnamed: C116.1, R130.1, R131.2, U104.1 (ADJ)
unnamed: D101.1 (K), D102.1 (K), Q102.1 (G), R112.2, R113.2
unnamed: D101.2 (A), R112.1, R114.2
unnamed: D103.2 (A), R120.2
unnamed: D104.1 (K), U102.7 (~CHRG)
unnamed: D104.2 (A), R125.2
unnamed: D105.3 (K), R129.1, R132.2
unnamed: D106.1 (K), U105.2
unnamed: D106.2 (A), R126.1
unnamed: D109.1 (K), U105.1
unnamed: D109.2 (A), R127.1
unnamed: D112.1 (K), U105.13
unnamed: D112.2 (A), R128.1
unnamed: Q101.1 (G), R110.1, R111.2
unnamed: Q101.2 (D), Q102.2 (D)
unnamed: R110.2, U101.12 (DSG)
unnamed: R114.1, U101.13 (CHG)
unnamed: R115.1, U101.22 (PRES)
unnamed: R116.1, TH101.1, TH102.1, U101.18 (TS)
unnamed: R116.2, U101.19 (VTB)
unnamed: R117.2, U101.17 (OCDP)
unnamed: R118.2, U101.14 (LD)
unnamed: R119.2, U101.16 (CBI)
unnamed: R121.1, R122.2, U102.9 (FB)
unnamed: R122.1, U102.8 (FBG)
unnamed: R124.2, U102.3 (PROG)
unnamed: R132.1, R133.2, U105.5 (+)
unnamed: R133.1, R134.2, U105.7 (+)
unnamed: R134.1, R135.2, U105.11 (+)
unnamed: R136.1, R137.2, U105.4 (-), U105.6 (-), U105.10 (-)

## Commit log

2022-01-10 added i2c temperature sensor and eeprom
    [ADRmu.kicad_pcb, ADRmu.kicad_sch, dcdc.kicad_sch, ref.kicad_sch]
2022-01-12 started proto area
    [ADRmu.kicad_pcb, ADRmu.kicad_sch, ref.kicad_sch]
2022-01-12 added 10V buffer
    [ADRmu.kicad_pcb, ADRmu.kicad_sch, ref.kicad_sch]
2022-01-12 the small reset
    [ADRmu.kicad_pcb, ADRmu.kicad_sch, dcdc.kicad_sch, ref.kicad_sch]
2022-01-13 getting there ...
    [ADRmu.kicad_pcb]
2022-01-13 send halp
    [ADRmu.kicad_pcb, ADRmu.kicad_sch, ref.kicad_sch]
2022-01-13 net classes
    [ADRmu.kicad_pcb, ADRmu.kicad_sch, dcdc.kicad_sch, ref.kicad_sch]
2022-01-13 trace widths based on net classes
    [ADRmu.kicad_pcb, ref.kicad_sch]
2022-01-14 flood of prototyping area
    [ADRmu.kicad_pcb, ADRmu.kicad_sch, ref.kicad_sch]
2022-01-14 reference designators reassigned
    [ADRmu.kicad_pcb, ADRmu.kicad_sch, dcdc.kicad_sch, ref.kicad_sch]
2022-01-14 added common mode filter
    [ADRmu.kicad_pcb, ADRmu.kicad_sch, dcdc.kicad_sch]
2022-01-14 generated bom, pdf, gerbers
    [ADRmu-B_Cu.gbr, ADRmu-B_Mask.gbr, ADRmu-B_Paste.gbr, ADRmu-B_Silkscreen.gbr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]
2022-01-14 added some dubious copper rings
    [ADRmu-B_Cu.gbr, ADRmu-B_Mask.gbr, ADRmu-B_Paste.gbr, ADRmu-B_Silkscreen.gbr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]
2022-01-14 added dubious flightless birb
    [ADRmu-B_Cu.gbr, ADRmu-B_Mask.gbr, ADRmu-B_Paste.gbr, ADRmu-B_Silkscreen.gbr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]
2022-01-30 Obligatory bugs in the first production run:
    - Missing stability cap between buffer out and -in
    - Missing cap for autozeroing buffer
    - Side status LEDs need to be flipped
    - Many schematic net names wrong
    - LDO power good implemented wrong
    [ADRmu.kicad_pcb, ADRmu.kicad_sch, dcdc.kicad_sch, ref.kicad_sch]
2022-02-01 GNDf terminal was sharing a via with heater return
    [ADRmu.kicad_pcb, ADRmu.kicad_sch, dcdc.kicad_sch, ref.kicad_sch]
2022-02-02 schematics updated to rev.2
    [ADRmu.kicad_pcb, ADRmu.kicad_sch, dcdc.kicad_sch, ref.kicad_sch]
2022-02-04 added xml bom
    [ADRmu.csv]
2022-02-10 adding prec resistor alternatives
    [ADRmu.kicad_pcb, ADRmu.kicad_sch, dcdc.kicad_sch, ref.kicad_sch]
2022-02-11 goodbye proto area, hello resistor networks
    [ADRmu.kicad_pcb, ADRmu.kicad_sch, dcdc.kicad_sch, ref.kicad_sch]
2022-02-11 Rev 0.3
    [ADRmu.kicad_pcb, ADRmu.kicad_sch, dcdc.kicad_sch, ref.kicad_sch]
2022-02-11 new folder structure to accommodate battery module
    [ADRmu-B_Cu.gbr, ADRmu-B_Mask.gbr, ADRmu-B_Paste.gbr, ADRmu-B_Silkscreen.gbr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]
2022-02-12 switched to addressable eeprom
    [ADRmu.kicad_pcb, ADRmu.kicad_sch, dcdc.kicad_sch]
2022-02-12 I shall waste not a copper
    [ADRmu.kicad_pcb]
2022-02-12 rs-274x gerbers
    [ADRmu-B_Cu.gbr, ADRmu-B_Mask.gbr, ADRmu-B_Paste.gbr, ADRmu-B_Silkscreen.gbr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]
2022-02-12 started battery module
    [ADRmu_battery.kicad_pcb, ADRmu_battery.kicad_sch]
2022-02-13 backplane connector changes
    [ADRmu-B_Cu.gbr, ADRmu-B_Mask.gbr, ADRmu-B_Paste.gbr, ADRmu-B_Silkscreen.gbr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]
2022-02-14 Battery charger Rev 0.1 finished
    [ADRmu_battery-B_Cu.gbr, ADRmu_battery-B_Mask.gbr, ADRmu_battery-B_Paste.gbr, ADRmu_battery-B_Silkscreen.gbr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]
2022-02-18 started Rev. 0.4 with better 1k/12k divider
    [ADRmu.kicad_sch, ref.kicad_sch]
2022-02-28 new TODOs after rev. 3 board assembly -_-
2022-03-03 rev 0.4 layout step
    [ADRmu.kicad_pcb, ADRmu.kicad_sch, dcdc.kicad_sch, ref.kicad_sch]
2022-03-03 rev 0.4 layout done
    [ADRmu.kicad_pcb]
2022-03-28 dimmed LED brightness and started to fix a few first generation battery bug fixes
    [ADRmu.kicad_pcb, ADRmu.kicad_sch, ADRmu_battery.kicad_sch, dcdc.kicad_sch]
2022-04-07 Battery module Rev 0.2
    [ADRmu.kicad_sch, ADRmu_battery-B_Cu.gbr, ADRmu_battery-B_Mask.gbr, ADRmu_battery-B_Paste.gbr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]
2022-04-09 Lowered Vreg to 11V to keep things cooler
    [ADRmu.csv, ADRmu.kicad_pcb]
2022-05-16 prepared rev 0.3 battery module with fuel gauge
    [ADRmu_battery.kicad_sch]
2022-05-16 battery module rev 0.3 routed
    [ADRmu_battery-B_Cu.gbr, ADRmu_battery-B_Mask.gbr, ADRmu_battery-B_Paste.gbr, ADRmu_battery-B_Silkscreen.gbr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]
2022-05-22 Reference board Rev 0.5 schematic
    [ADRmu.kicad_sch, dcdc.kicad_sch, ref.kicad_sch]
2022-05-23 Rev 0.5 routed
    [ADRmu-B_Cu.gbr, ADRmu-B_Mask.gbr, ADRmu-B_Paste.gbr, ADRmu-B_Silkscreen.gbr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]
2022-05-23 No longer configured for PRND by default
    [ADRmu-B_Cu.gbr, ADRmu-B_Mask.gbr, ADRmu-B_Paste.gbr, ADRmu-B_Silkscreen.gbr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]
2022-06-03 minor bug fixes for battery module
    [ADRmu_battery.kicad_pcb, ADRmu_battery.kicad_sch]
2022-06-04 Battery module Rev 0.4 routed
    [ADRmu_battery-B_Cu.gbr, ADRmu_battery-B_Mask.gbr, ADRmu_battery-B_Paste.gbr, ADRmu_battery-B_Silkscreen.gbr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]
2022-07-11 Battery module Rev 0.6 update
    [ADRmu_battery-B_Cu.gbr, ADRmu_battery-B_Mask.gbr, ADRmu_battery-B_Paste.gbr, ADRmu_battery-B_Silkscreen.gbr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]
2022-08-15 New backplane, Reference Rev 0.6 with heated resistor network support
    [ADRmu-B_Cu.gbr, ADRmu-B_Mask.gbr, ADRmu-B_Paste.gbr, ADRmu-B_Silkscreen.gbr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]
2022-08-23 Rev 0.2 Backplane
    [backplane-B_Cu.gbr, backplane-B_Mask.gbr, backplane-B_Paste.gbr, backplane-B_Silkscreen.gbr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]
2022-12-27 Ref module Rev. 0.9
    [ADRmu-B_Cu.gbr, ADRmu-B_Mask.gbr, ADRmu-B_Paste.gbr, ADRmu-B_Silkscreen.gbr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]
2023-01-01 restructures the folders and adds READMEs
    [backplane-B_Cu.gbr, backplane-B_Mask.gbr, backplane-B_Paste.gbr, backplane-B_Silkscreen.gbr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]
2023-01-01 adds cost estimate csv
    [adrmu6layer.kicad_sch, buf.kicad_sch, ref.kicad_sch, reference_single_desktop.csv]
2023-01-29 Rev. 1.0
    [adrmu6layer-B_Cu.gbr, adrmu6layer-B_Mask.gbr, adrmu6layer-B_Paste.gbr, adrmu6layer-B_Silkscreen.gbr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]
2023-02-01 New noise results
    [adrmu6layer.kicad_pcb]
2023-02-05 corrected noise measurements
    [adrmu6layer.kicad_pcb, adrmu6layer.kicad_sch, buf.kicad_sch, ref.kicad_sch]
2023-02-17 Rev 1.1 & Kicad 7 update
    [adrmu6layer-B_Cu.gbr, adrmu6layer-B_Mask.gbr, adrmu6layer-B_Paste.gbr, adrmu6layer-B_Silkscreen.gbr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]
2023-02-19 Remade all 0.1 ... 10 Hz noise tests with new preamp
2023-03-09 Rev 1.2
    [adrmu6layer-B_Cu.gbr, adrmu6layer-B_Mask.gbr, adrmu6layer-B_Paste.gbr, adrmu6layer-B_Silkscreen.gbr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]
